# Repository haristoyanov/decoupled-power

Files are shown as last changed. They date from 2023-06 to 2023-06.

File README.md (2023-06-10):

# Linear Decoupled Power Supply

The goal of this project is to create a low-noise, decoupled power supply to power sensitive instrumentation in experimental research laboratories. This power supply will turn 120 VAC wall power into clean, adjustable output DC power, as well as break potential ground loops by being decoupled from the wall power by an isolation barrier. 

This power supply was designed by Mark Carlson at UBC, and we are closely following his original schematics.

# Table of Contents 
- [Motivation](#Motivation)
- [Parts List](#Parts-List)
- [Schematic](#Schematic)
- [Testing](#Testing)
- [Outlook](#Outlook)
- [Acknowledgements](#Acknowledgements)

# Motivation

Low noise, ground-decoupled DC is important for powering ADC/DACs and preamplifiers without introducing noise to the extremely sensitive measurement signals in an experimental condensed matter lab. Currently, the options are a stock DC power supply and a battery power supply. It is possible to improve on the DC power supply in terms of noise level, and the battery (while having low noise) has to be charged and has an unpredictable and possibly dangerous failure mode.
<div align="center">
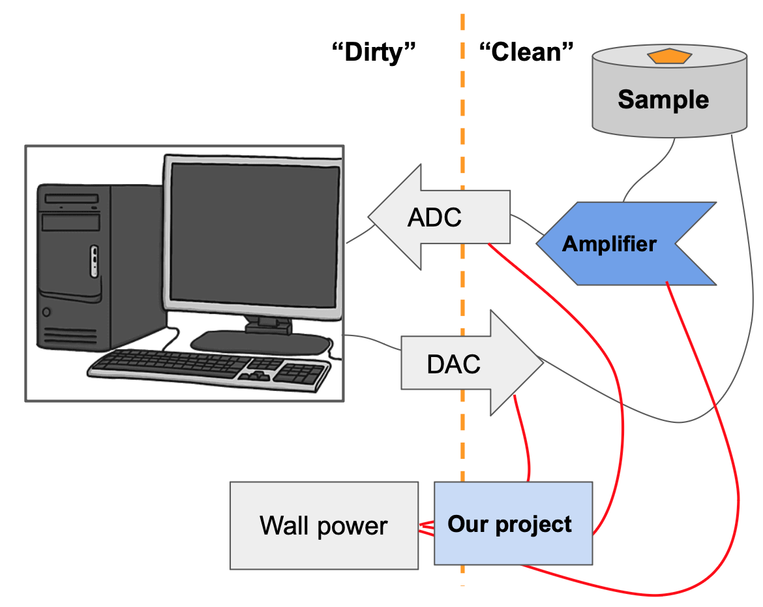
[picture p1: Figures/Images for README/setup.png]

</div>
</div>
<br/>
<br/>

# Parts List 
Below is a list of all circuit parts used for this project, excluding the Printed Circuit Boards themselves, which were ordered from OSHpark. The PCB design and schematics are included in the PCB folder of this repository. 

<div align="center">
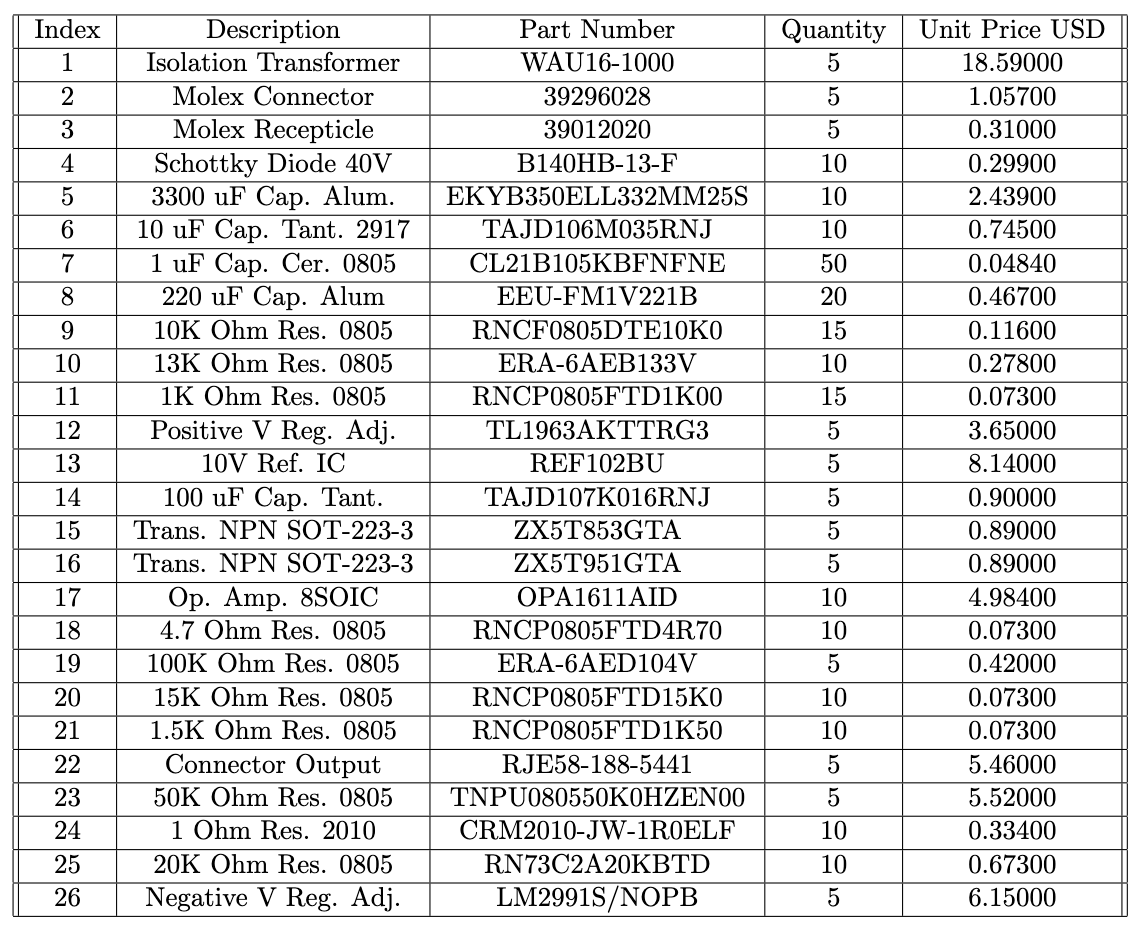
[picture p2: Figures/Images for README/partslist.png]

</div>

<br/>
<br/>

# Schematic 

This summary explains the relevant parts of the circuit from left to right.
1. The transformer takes wall power (120V AC at 60Hz) and outputs 16V AC at 60 Hz. This is the input to the power supply.
2. The diodes rectify the current, so that the top branch always has positive voltage and the bottom branch always has negative voltage.
3. The positive and negative voltage regulator ICs (TL1963A and LM2991, respectively) are supplied by the rectified AC, and decoupled using the capacitors to ground (filtering high-frequency noise and preventing output coupling to spikes or dips in the input AC). These output a DC voltage, with a shutdown (SHDN) indicator to show if they are working.
4. The exact output voltage is determined by the voltage on the ADJ pin. The 13K/1K voltage divider sets an output voltage of ±16 V on each branch.
5. The second stage of the circuit is powered by the ±16V. The first component is the 10V voltage reference IC (REF102), which outputs a more precise DC voltage than a voltage regulator. However, it only allows small current draw.
6. To set the exact output voltage, the two op-amp ICs (which are powered from the ±16V DC) take the 10V input from the voltage reference and output a voltage set by the voltage divider consisting of R35 and R36. In the given schematic, this outputs 15V from the top branch and -15V from the bottom.
7. The second op-amp matches and inverts the output of the first, ensuring a linear relationship between the positive and negative output.
8. The two transistors (Q30 and Q31) allow for more current draw from the 16V supply. This current is limited by the voltage regulator ICs, which allow 1A of current to flow.
9. The output goes through an Ethernet-style connector, whose indicator lights indicate whether each branch is outputing a voltage.

<div align="center">
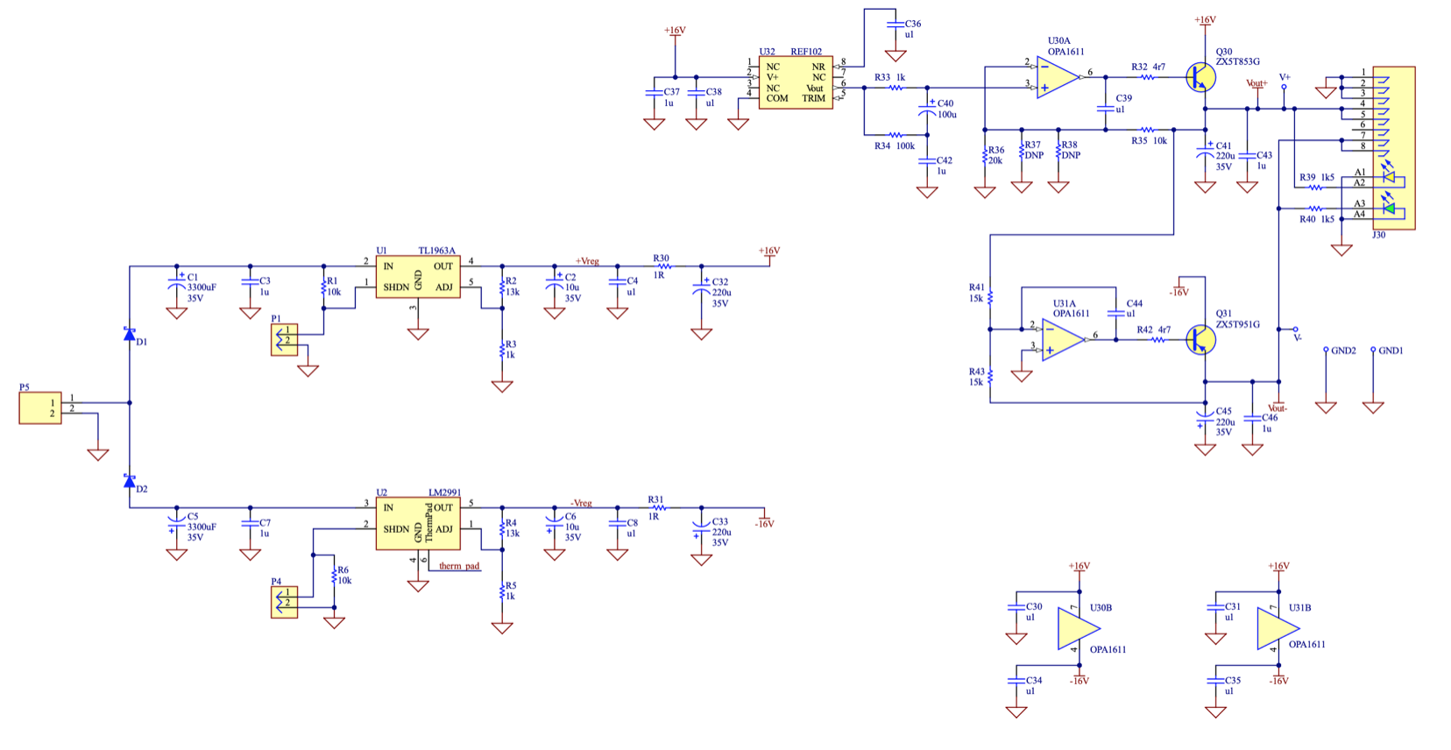
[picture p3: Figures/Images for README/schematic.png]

</div>

# Testing

The first testing after confirming a ±15V DC output involved determining the Power Supply Rejection Ratio (PSRR), which describes how well the power supply attenuates noise at a frequency of interest. The PSRR is defined as the 20 times the logarithm of the input to output voltage ripple ratio at 60 Hz. As such, an ideal DC power supply has an infinite PSRR.

<div align="center">
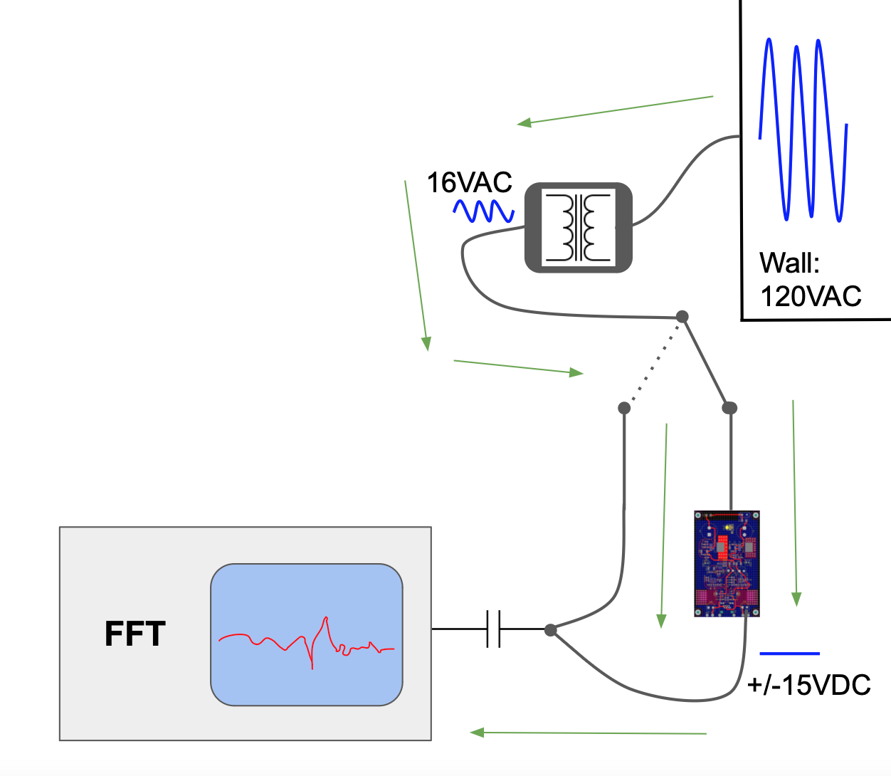
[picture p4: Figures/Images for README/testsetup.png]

</div>

The testing was conducted through a capacitor to the analog input of a Stanford Research Systems SR1 spectrum analyzer.

Preliminary results indicate a power supply rejection ratio (from 120V AC wall power) of approximately 160. This compares to roughly 100 for the DC power supply that is currently used (Acopian TD15-40, estimated from the voltage ripple quoted in its datasheet). Below is a graph of root-mean-squared Voltage versus frequency on logarithmic axes for a narrow range of frequencies around 60 Hz. We used the data displayed in this plot to calculate our PSRR. 

<div align="center">
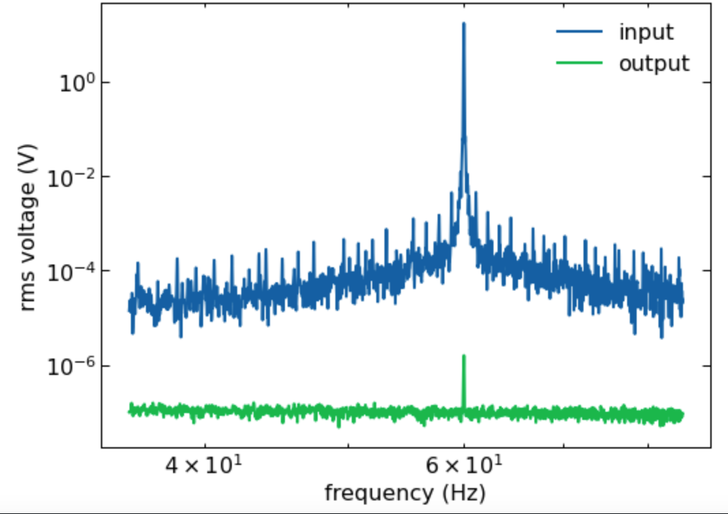
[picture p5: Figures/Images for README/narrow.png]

</div>

<br />
<br />
It is also of interest to examine the performance of our power supply at a wide range of frequencies. Below is a plot of the voltage noise spectral density (V/rtHz) against the frequency (Hz) on logarithmic axes for a frequency range of 0 Hz to 1500 Hz. To get the total voltage noise in a certain bandwidth, one must integrate the square of the spectral density across that bandwidth and then take the square root of the result. After performing a rough integration across a bandwidth ranging from 10 Hz to 1500 Hz using the method described above, we found that the total voltage noise was reduced by a factor of approximately 100,000.

<div align="center">
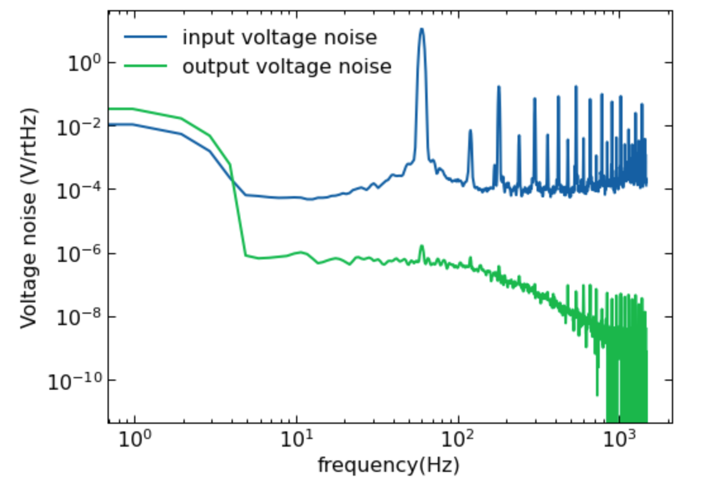
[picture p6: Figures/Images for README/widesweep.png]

</div>

<br />
<br />

More figures and the code used to analyze this data can be found in the appropriately named folders of this repository. 

# Outlook
We will machine protective boxes for convenience. Also, we will try to implement potentiometers to create an adjustable output.

# Acknowledgements
Thank you to the instructors, TAs, and our classmates for UCSB PHYS 13CL/CS15C, thank you to the Dr. Young and all the Young lab grad students and postdocs that helped us, and thank you to Dr. Folk and Mark Carlson at UBC for the schematics and designs.

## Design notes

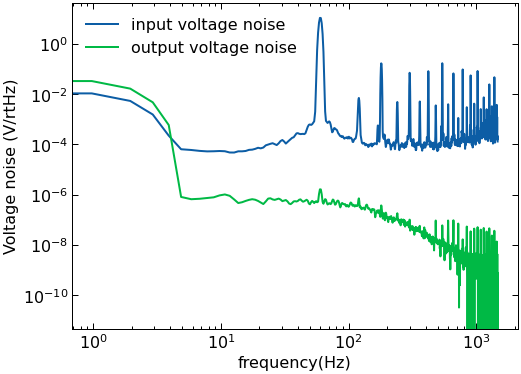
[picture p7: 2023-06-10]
Figures/spectral_density.png

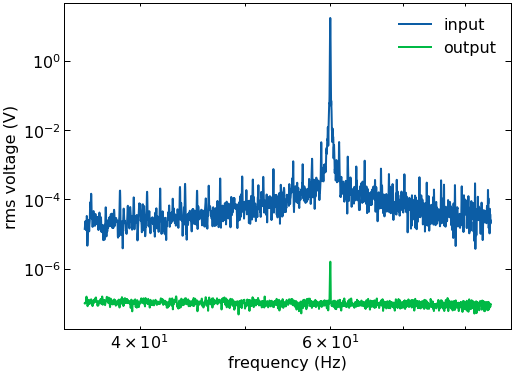
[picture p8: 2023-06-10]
Figures/Vrms_PSRR_calc.png

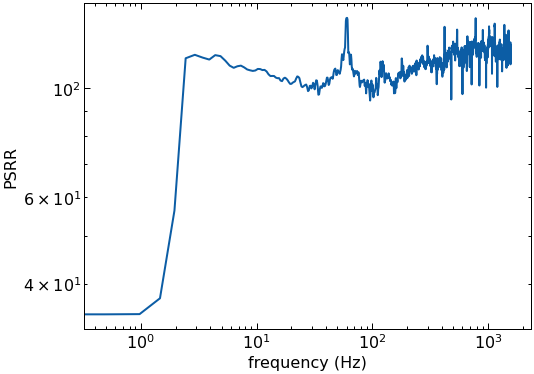
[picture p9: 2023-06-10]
Figures/Vrms_PSRR_widesweep.png

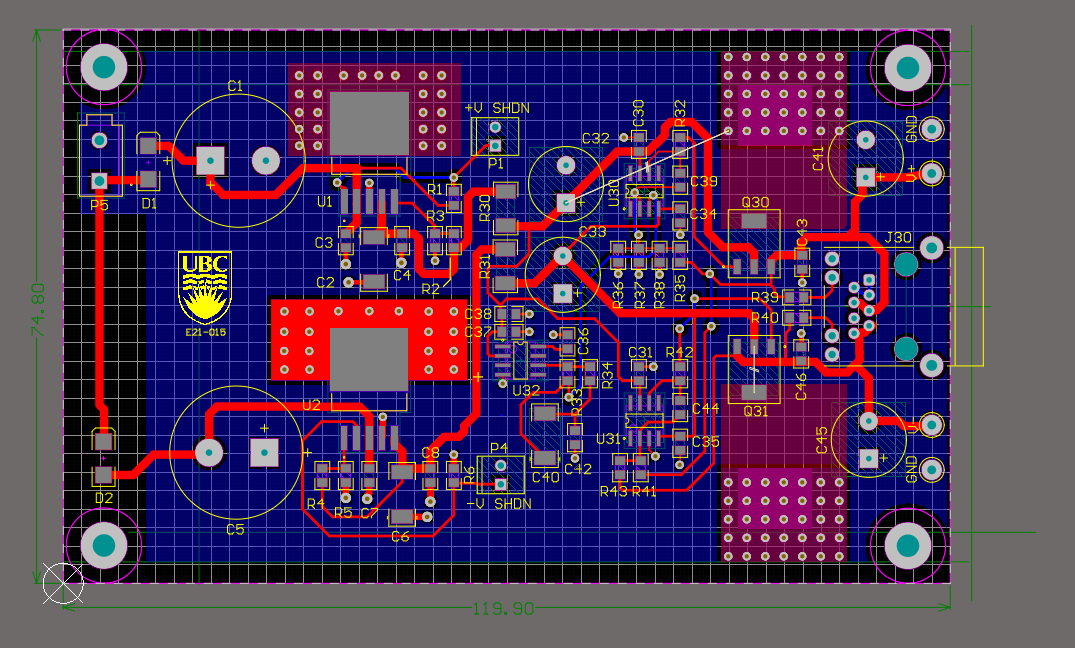
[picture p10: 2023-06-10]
PCB/PS PCB.PNG

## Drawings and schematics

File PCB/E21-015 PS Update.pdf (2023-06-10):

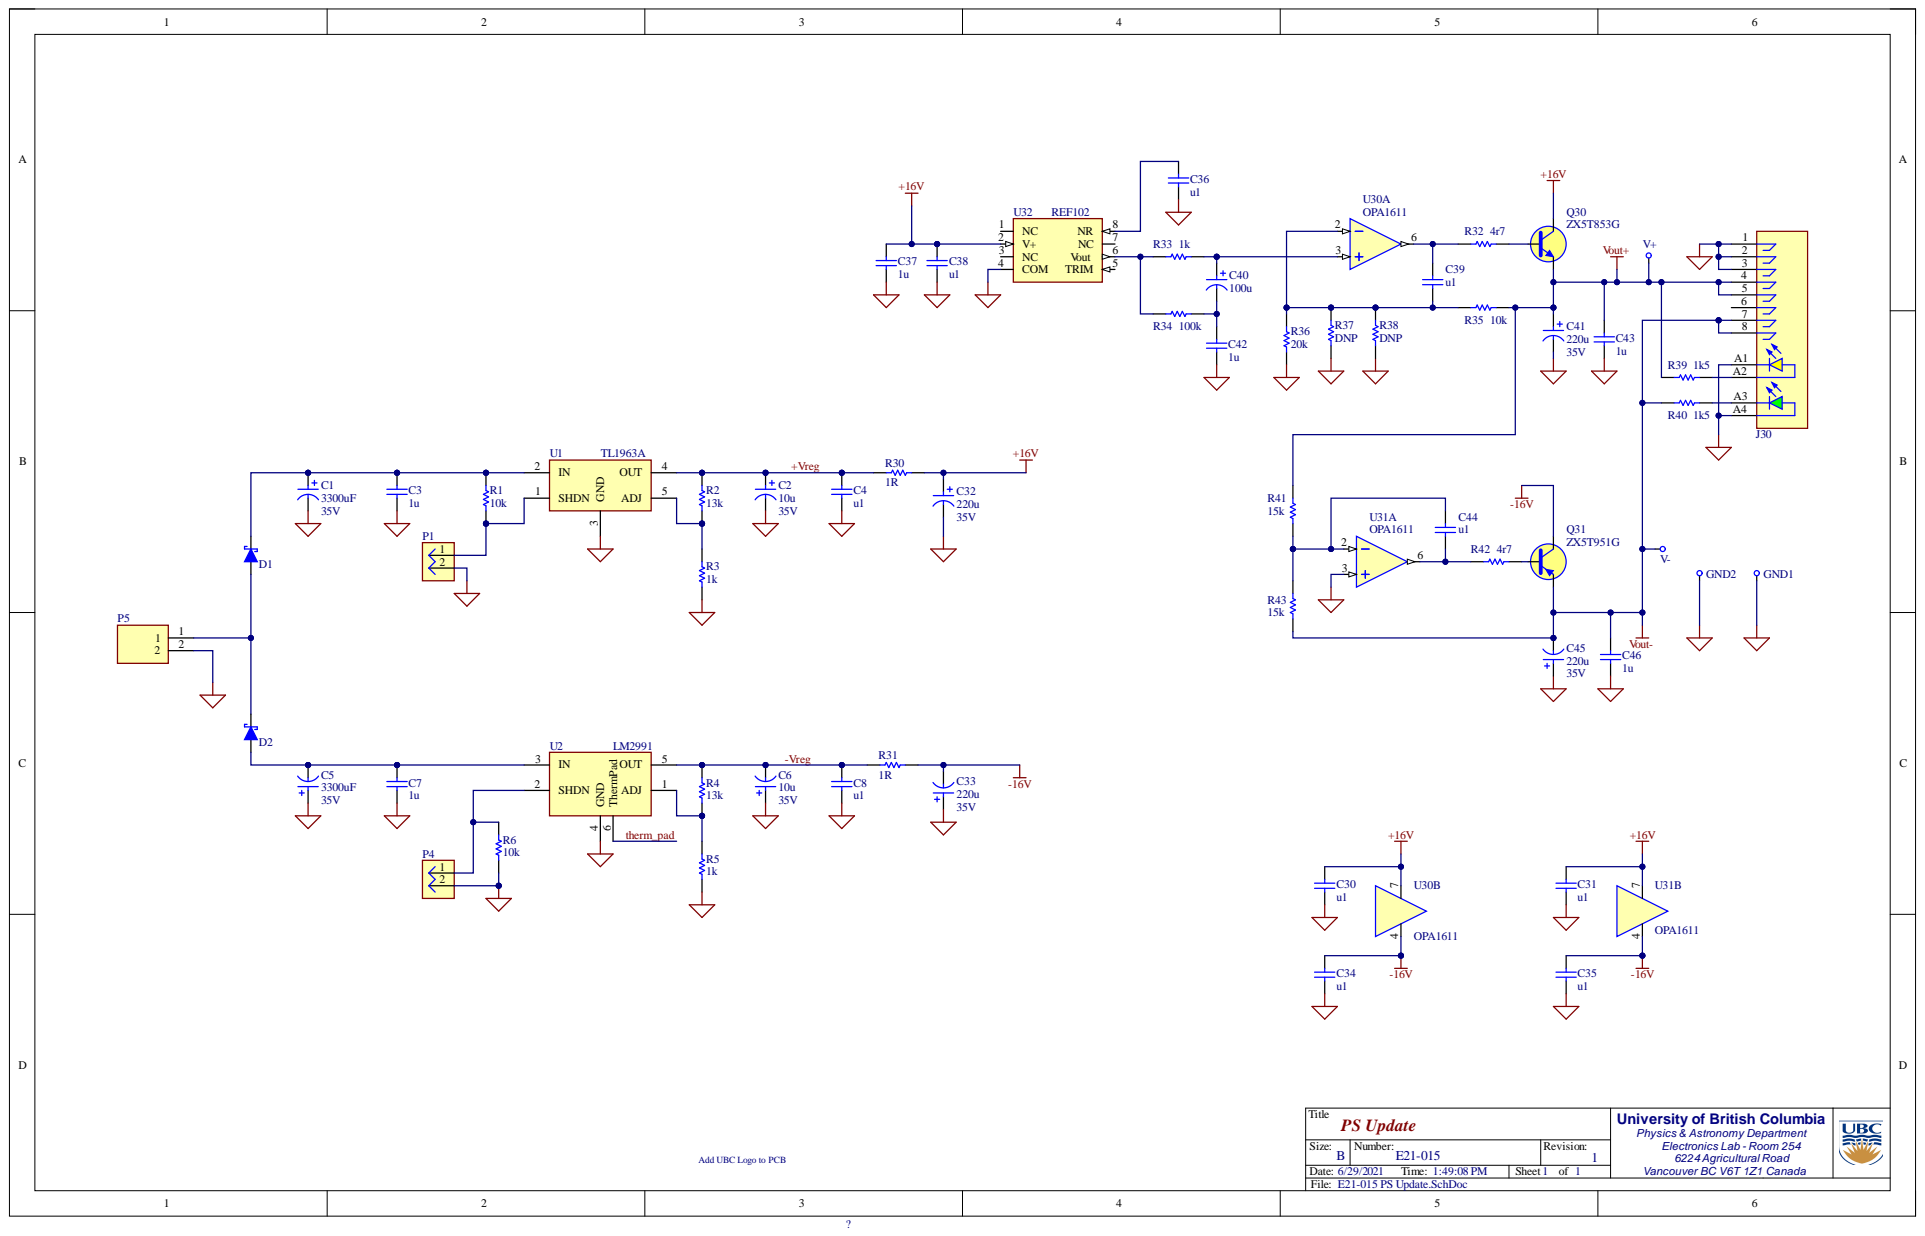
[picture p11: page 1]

Ti tl e PS Up | Universit y o f British Colu m bia P h ys i c s & A s tro n o m y D e p a rtm e n t El e c tro n i c s L a b -R o o m 2 5 4 62 2 4 A g ri c u l tu ra l R o a d Va n c o u v e r B C V6 T 1 Z 1 C a n a da

Si z e : B | N umber : -0 1 5 | Revi s i on:

Dat e : Ti me: | Sheet 1 of 1

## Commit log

2023-05-31 Create pcB
2023-06-10 Create RMS Voltage PSSR Calculation
